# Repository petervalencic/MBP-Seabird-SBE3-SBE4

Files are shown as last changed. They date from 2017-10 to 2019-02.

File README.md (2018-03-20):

# Arduino Seabird SBE3 SBE4 

The project contains C/C++ code for Ardiuno Uno and a shield (Eagle project) for SBE-3 and SBE-4 

# SBE 3
Intended primarily for use on moored and fixed-site temperature measuring systems, the SBE 3S can also be used as a component in custom systems or for high-accuracy industrial and environmental temperature monitoring applications. The low noise characteristics of the SBE 3S allow the use of hybrid frequency measuring techniques to obtain rapid sampling with very high resolution; 40 μ°C resolution can be readily obtained at a 6 Hz sampling rate.

CALIBRATION EQUATION

The calibration yields four coefficients (g, h, i, j) that are used in the following equation (Bennett, 1972):

T [°C] = [1 / (g + hln(fo/f) + iln²(fo/f) + jln³(fo/f) )] - 273.15

where T is temperature [°C], ln is natural log function, and f is SBE 3S output frequency [Hz]. Note that fo, an arbitrary scaling term used for purposes of computational efficiency, was historically chosen as the lowest sensor frequency generated during calibration. For calibration results expressed in terms of ITS-90 temperatures, fo is set to 1000. Calibration fit residuals are typically less than 0.0001 °C.

Example Calibration Data (sensor serial number 2213, 30 May 1996):
g = 4.28793855e-03     h = 6.25807786e-04     i = 2.19368239e-05     j = 1.84262924e-06     f0 = 1000.000

# SBE 4
The SBE 4 conductivity sensor is a modular, self-contained instrument that measures conductivity from 0 to 7 S/m, covering the full range of lake and oceanic applications. The sensor has electrically isolated power circuits and optically coupled outputs to eliminate any possibility of noise and corrosion caused by ground loops. Interfacing is also simplified by the square-wave variable frequency output signal (nominally 2.5 to 7.5 kHz, corresponding to 0 to 7 S/m). The sensor offers improved temperature compensation, smaller fit residuals, and faster turn-on stabilization times.

Because of the SBE 4’s low noise characteristics, hybrid frequency measuring techniques (used in Sea-Bird’s CTD instruments) provide rapid sampling with very high temporal and spatial resolution.

CALIBRATION EQUATION

A least-squares fitting technique (including a zero conductivity point in air) yields calibration coefficients for use in the following equation:

Conductivity [S/m] = ( g + hf 2 + if 3+ jf 4 ) / 10 (1 + dt + ep)

where f is instrument frequency [kHz], t is temperature [°C], p is pressure [decibars], and d is thermal coefficient of expansion (3.25 x 10 -06) and e is bulk compressibility (-9.57 x 10 -08) of the borosilicate cell. The resulting coefficients g, h, i, and j are listed on the calibration certificate. Residuals are typically less than 0.0002 S/m.

Example Calibration Data (sensor serial number 2020, 30 May 1997)

Practical Salinity Scale 1978: C(35,15,0) = 4.2914 [S/m]

g = -1.05697877e+01    h = 1.42707291e+00    i = -4.32023820e-03    j = 4.53455585e-04

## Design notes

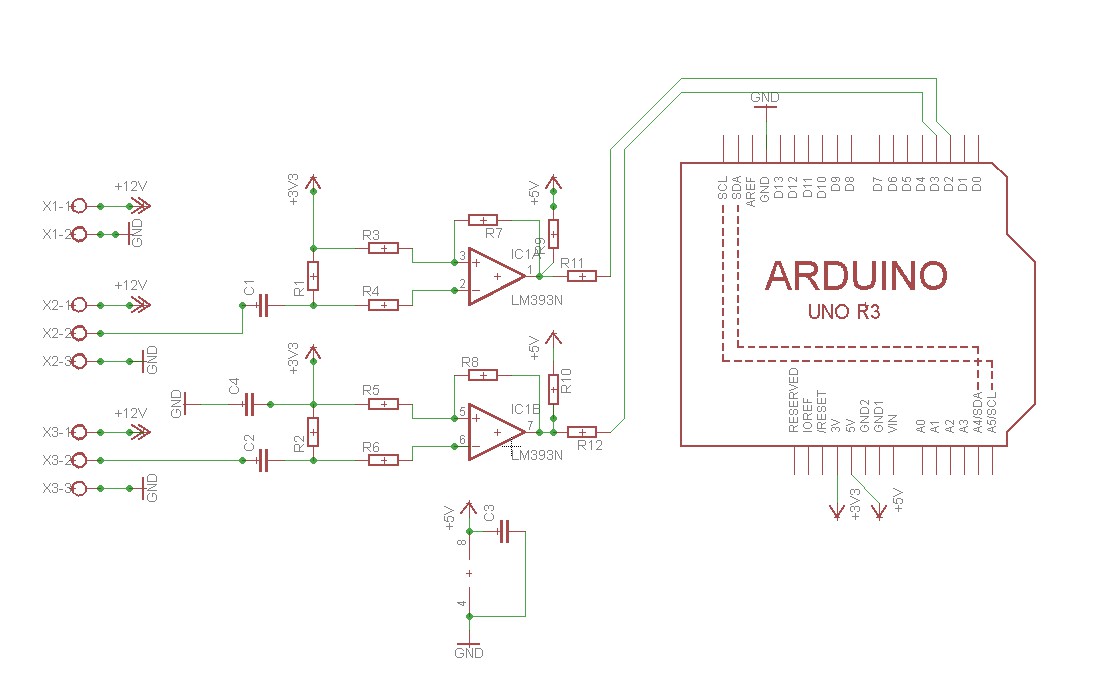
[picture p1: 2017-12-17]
EagleShield/screenshot_1710.jpg

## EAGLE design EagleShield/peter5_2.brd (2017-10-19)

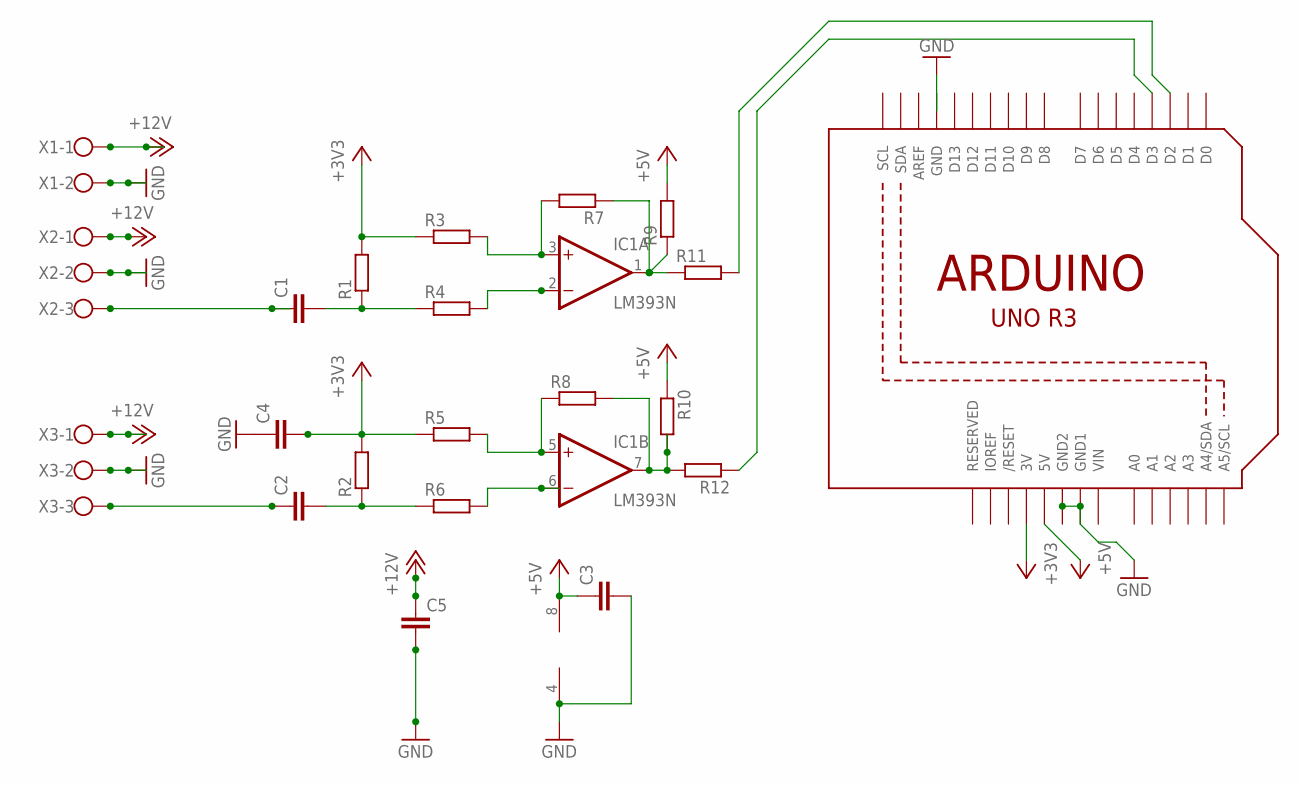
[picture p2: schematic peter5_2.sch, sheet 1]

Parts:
C1, C2, C3, C4: C-EU025-040X050; C025-040X050
C5: C2.5/2; C2.5-2
IC1: LM393N; DIL08; MPN LM393N...
R1, R2, R3, R4, R5, R6, R7, R8, R9, R10, R11, R12: R-EU_0207/7; 0207/7
U1: ARDUINOR3-BPLACE
X1: W237-102
X2, X3: W237-103

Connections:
+3V3: C4.2, R1.2, R2.2, R3.1, R5.1, U1.3V
+5V: C3.1, IC1.8 (V+), R9.2, R10.1, U1.5V
+12V: C5.1, X1.1, X2.1, X3.1
GND: C3.2, C4.1, C5.2, IC1.4 (V-), U1.GND, X1.2, X2.2, X3.2
GND1: U1.GND1
GND2: U1.GND2
unnamed: IC1.3 (+IN), R3.2, R7.2
unnamed: IC1.2 (-IN), R4.2
unnamed: IC1.1 (OUT), R7.1, R9.1, R11.1
unnamed: R11.2, U1.D2
unnamed: R12.1, U1.D3
unnamed: C1.2, R1.1, R4.1
unnamed: IC1.7 (OUT), R8.2, R10.2, R12.2
unnamed: C2.1, X3.3
unnamed: IC1.5 (+IN), R5.2, R8.1
unnamed: IC1.6 (-IN), R6.2
unnamed: C2.2, R2.1, R6.1
unnamed: C1.1, X2.3
VIN: U1.VIN

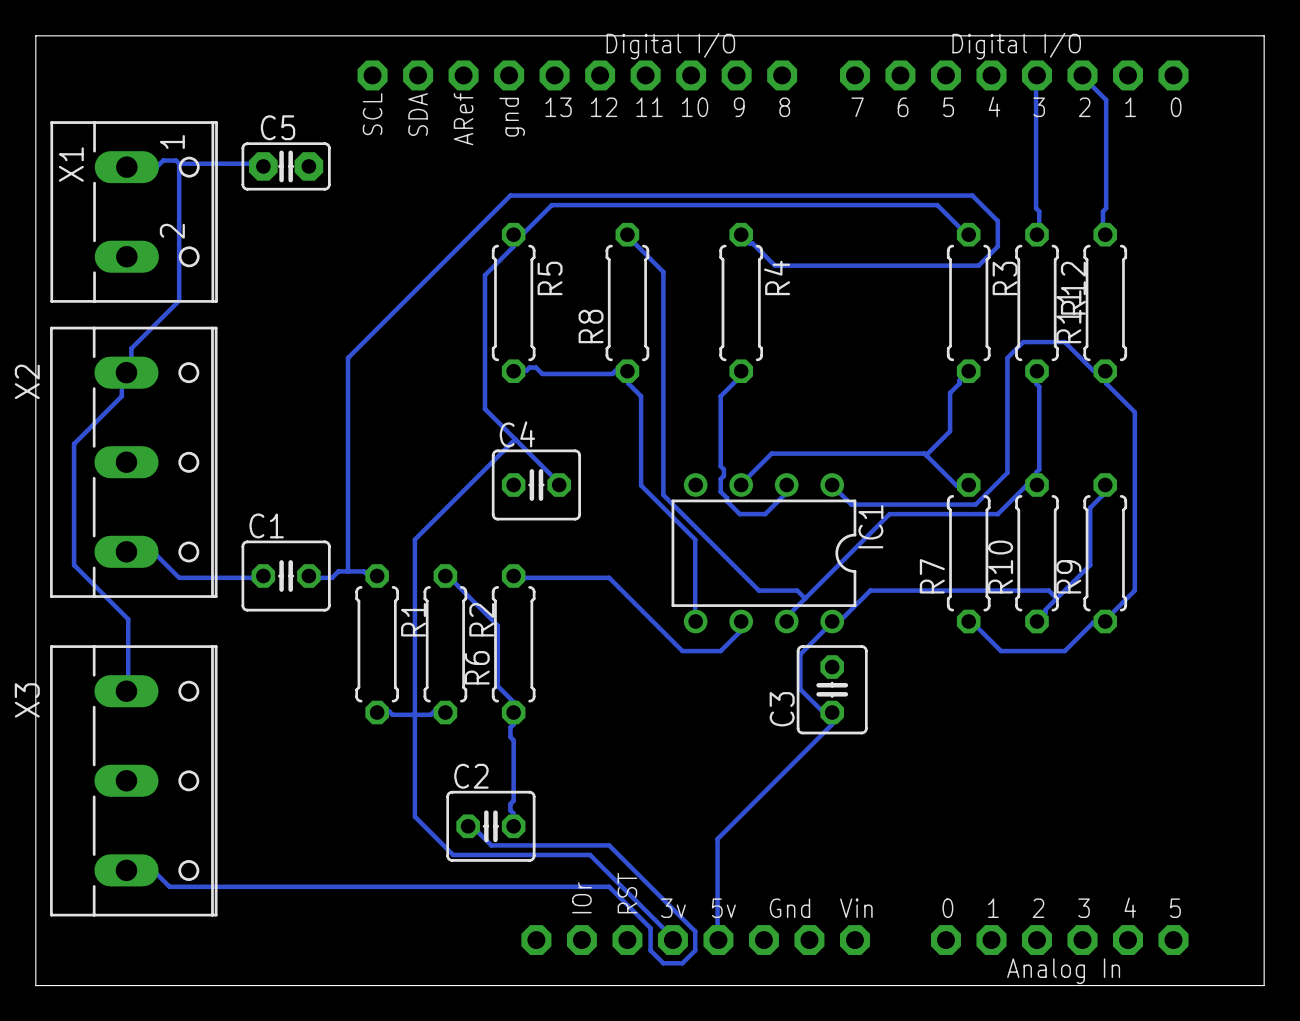
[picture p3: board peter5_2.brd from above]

Board: 2 copper layers, 68.6 x 53.0 mm, 22 parts (0 on the bottom side), 16 nets.

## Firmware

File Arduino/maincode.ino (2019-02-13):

/*****************************************************************
   Merjenje temperature in slanosti s pomočjo
   temperaturne sonde SeaBird SBE-3,
   sonde za slanost Seabird SBE-4 ter miktonotrolerja
   Arduino UNO

   Peter Valenčič, 05.12.2017

   1.) Sprememba preračuna slanosti iz prevodnosti, 15.04.2018
   2.) Dodan Access-Control-Allow-Origin: *, 12.08.2018
 ****************************************************************/

#include < SPI.h > #include < SD.h > #include < Ethernet.h >

//mrežne nastavitve
byte myMac[6];
byte myIP[4];
byte myNM[4];
byte myGW[4];
byte myDNS[4];

//priključne sponke za SBE3 in SBE4
const byte interruptPinTemp = 2;
const byte interruptPinPrevodnost = 3;

//konstante za SBE3
//Kalibrirano Sea-Bird GmbH, SBE3 T121219Mar16
const double g_sbe3 = 4.85442486e-003;
const double h_sbe3 = 6.77400494e-004;
const double i_sbe3 = 2.65502731e-005;
const double j_sbe3 = 2.06782794e-006;
const double f_sbe3 = 1000;

//konstante za SBE4
//Kalibrirano Sea-Bird GmbH, SBE4 C141601Mar16
const double g_sbe4 = -4.10731453e+000;
const double h_sbe4 = 5.02267656e-001;
const double i_sbe4 = -1.63378659e-004;
const double j_sbe4 = 3.70269818e-005;
const double f_sbe4 = 1000;
const double Pcor = -9.5700e-008;
const double Tcor = 3.2500e-006;
const double p = 0;

//pomožne spremenljivke
int timer1_counter;
int cnt_temp = 0;
int cnt_prevodnost = 0;

//frekvenca iz SBE3 in SBE4
int f_temp = 0;
int f_prevodnost = 0;

boolean bPrvaMeritev = false;

boolean bTest = false;

EthernetServer server = EthernetServer(80);

void setup() {
  Serial.begin(9600);
  noInterrupts(); //prekinemo izvajanje interruptov
  //delay(50);
  //določimo vhode za branje frekvence
  pinMode(interruptPinTemp, INPUT_PULLUP);
  pinMode(interruptPinPrevodnost, INPUT_PULLUP);

  //določimo metodo, ki se bo ob prekinitvi izvedla
  attachInterrupt(digitalPinToInterrupt(interruptPinTemp), beriTemperaturo, CHANGE);
  attachInterrupt(digitalPinToInterrupt(interruptPinPrevodnost), beriPrevodnost, CHANGE);

  //nastavimo časovno prekinitev na 1 sekundo pri taktu 16 MHz
  TCCR1A = 0;
  TCCR1B = 0;
  timer1_counter = 34286; // preload timer 65536-16MHz/256/2Hz

  TCNT1 = timer1_counter; // preload timer
  TCCR1B |= (1 << CS12); // 256 prescaler
  TIMSK1 |= (1 << TOIE1); // enable timer overflow interrupt

  // preveri če obstaja SD kartica
  if (!SD.begin(4)) {
    Serial.println("SD card not present...");
    return;
  }

  //prebere datoteko networ.txt, v njej so shranjene mrežne nastavitve
  File fh = SD.open("network.txt", FILE_READ);
  char netBuffer[32];

  int chPos = 0;
  int lineNo = 0;

  //sprehodimo se skozi vse zapise v datoteki in ustrezno zapišemo vrednosti
  while (fh.available()) {
    char ch = fh.read();
    if (ch == '\n') {
      chPos = 0;
      switch (lineNo) {
      case 0:
        if (getMAC(netBuffer, myMac)) Serial.println(F("mac ok"));
        break;

      case 1:
        if (getIP(netBuffer, myIP)) Serial.println(F("ip ok"));
        break;

      case 2:
        if (getIP(netBuffer, myNM)) Serial.println(F("netmask ok"));
        break;

      case 3:
        if (getIP(netBuffer, myGW)) Serial.println(F("gateway ok"));
        break;

      case 4:
        if (getIP(netBuffer, myDNS)) Serial.println(F("dns ok"));
        break;
      }

      lineNo++;
    } else if (ch == '\r') {
      // do nothing
    } else if (chPos < 31) {
      netBuffer[chPos] = ch;
      chPos++;
      netBuffer[chPos] = 0;
    }
  }

  fh.close();

  int x;

  Serial.println("mac ");
  for (x = 0; x < 6; x++) {
    Serial.print(myMac[x], HEX);
    if (x < 5) Serial.print(":");
  }

  Serial.println("ip ");
  for (x = 0; x < 4; x++) {
    Serial.print(myIP[x], DEC);
    if (x < 3) Serial.print(".");
  }

  Serial.println("nmsk ");
  for (x = 0; x < 4; x++) {
    Serial.print(myNM[x], DEC);
    if (x < 3) Serial.print(".");
  }

  Serial.println("gtw ");
  for (x = 0; x < 4; x++) {
    Serial.print(myGW[x], DEC);
    if (x < 3) Serial.print(".");
  }

  Serial.println("dns ");
  for (x = 0; x < 4; x++) {
    Serial.print(myDNS[x], DEC);
    if (x < 3) Serial.print(".");
  }

  Serial.println("Start");
  Ethernet.begin(myMac, myIP, myDNS, myGW, myNM);
  Serial.println(Ethernet.localIP());
  Serial.println("\r\nStart wbs");

  //startamo server socket
  server.begin();

  //omogočimo prekinitve
  interrupts();

}

/**
   Prekinitvena servisna rutina. Izvaja se 1x na sekundo
*/
ISR(TIMER1_OVF_vect) {

  if (bPrvaMeritev == false) return;

  TCNT1 += timer1_counter; //preload časovnika

  //frekvenca iz SBE3 in SBE4
  f_temp = cnt_temp;
  f_prevodnost = cnt_prevodnost;

  bTest = true;
  //resetiramo števce
  cnt_temp = 0;
  cnt_prevodnost = 0;

}

//števec, ki se povečuje v prekinitvi za temperaturo
void beriTemperaturo() {
  cnt_temp++;
}

//števec, ki se povečuje v prekinitvi za slanost
void beriPrevodnost() {
  cnt_prevodnost++;
}

//metoda preračuna temperaturo iz frekvence
double calcTemp(double frekvenca) {
  double f = frekvenca;
  if (f <= 0) return 0;
  double logRes = log(f_sbe3 / f);
  return (1.0 / (g_sbe3 + (h_sbe3 * logRes) + (i_sbe3 * pow(logRes, 2.0)) + (j_sbe3 * pow(logRes, 3.0))) - 273.15);
}

//metoda preračuna prevodnost S/m iz (frekvence in temperature)
double calcPrevodnost(double f, double temperatura) {
  double frek = f;
  double tmp = temperatura;
  if (frek <= 0) return 0;
  frek = frek / 1000; //frekvenco pretvorimo v kHz
  return (g_sbe4 + h_sbe4 * pow(frek, 2) + i_sbe4 * pow(frek, 3) + j_sbe4 * pow(frek, 4)) / 10 * (1 + Tcor * tmp + Pcor * p); //mS/cm = S/m * 10
}

//metoda za preračun slanosti PSU za podano temperaturo, prevodnost in tlak
double calcSlanost(double t, double c, double p) {
  if (c <= 0) return 0;
  double a0 = 0.008;
  double a1 = -0.1692;
  double a2 = 25.3851;
  double a3 = 14.0941;
  double a4 = -7.0261;
  double a5 = 2.7081;
  double b0 = 0.0005;
  double b1 = -0.0056;
  double b2 = -0.0066;
  double b3 = -0.0375;
  double b4 = 0.0636;
  double b5 = -0.0144;
  double k = 0.0162;

  double Aa1 = 2.070e-5;
  double Aa2 = -6.370e-10;
  double Aa3 = 3.989e-15;

  double Bb1 = 0.03426;
  double Bb2 = 0.0004464;
  double Bb3 = 0.4215;
  double Bb4 = -0.003107;

  double c0 = 0.6766097;
  double c1 = 0.0200564;
  double c2 = 0.0001104259;
  double c3 = -0.00000069698;
  double c4 = 0.0000000010031;

  double temp = 1.00024 * t;
  double R = c / 42.914;

  //double rt = c0 + c1 * temp + c2 * temp * temp + c3 * temp * temp * temp + c4 * temp * temp * temp * temp;
  double rt = c0 + c1 * temp + c2 * pow(temp, 2) + c3 * pow(temp, 3) + c4 * pow(temp, 4);

  //double alpha = (Aa1 * p + Aa2 * p * p + Aa3 * p * p * p) / (1 + Bb1 * temp + Bb2 * temp * temp + Bb3 * R + Bb4 * temp * R);
  double alpha = (Aa1 * p + Aa2 * pow(p, 2) + Aa3 * pow(p, 3)) / (1 + Bb1 * temp + Bb2 * pow(temp, 2) + Bb3 * R + Bb4 * temp * R);

  double Rt = R / (rt * (1 + alpha));

  double S = a0 + a1 * pow(Rt, 0.5) + a2 * Rt + a3 * pow(Rt, 1.5) + a4 * Rt * Rt + a5 * pow(Rt, 2.5) + (temp - 15) * (b0 + b1 * pow(Rt, 0.5) + b2 * Rt + b3 * pow(Rt, 1.5) + b4 * Rt * Rt + b5 * pow(Rt, 2.5)) / (1 + k * (temp - 15));

  return S;
}

//Glavna zanka programa
void loop() {

  //prvo meritev izpustimo
  if (bPrvaMeritev == false) {
    bPrvaMeritev = true;
    f_temp = 0;
    f_prevodnost = 0;
    return;
  }

  /*
    if (bTest == true)
    {

      Serial.print("temp:");
      Serial.println(f_temp);
      Serial.print("cond:");
      Serial.println(f_prevodnost);
      bTest = false;
    }
  */
  EthernetClient client = server.available();

  if (client) {
    boolean bTekocaVrstica = true;
    while (client.connected()) {
      if (client.available()) {
        char c = client.read();
        Serial.write(c);
        if (c == '\n' && bTekocaVrstica) {

          //dobimo temperaturo
          double local_temp = calcTemp(f_temp);

          //dobimo prevodnost S/m in preračunamo slanost
          double local_cond = calcPrevodnost(f_prevodnost, local_temp);

          //pri slanosti moramo enoto S/m množiti z 10 da dobimo mS/cm
          //predpostavimo da je tlak 0.2 dBar
          // double local_sal = calcSlanost(local_temp, (local_cond * 10), 0.2);

          client.println("HTTP/1.1 200 OK");
          client.println("Content-Type: text/xml");
          client.println("Access-Control-Allow-Origin: *");
          client.println("Connection: close");
          client.println();
          client.print("<?xml version='1.0' encoding='UTF-8'?><root><temp><value>");
          client.print(local_temp, 3);
          client.print("</value><freq>");
          client.print(f_temp);
          client.print("</freq></temp><sal><value>");
          client.print(calcSlanost(local_temp, (local_cond * 10), 0.2), 4);
          client.print("</value><freq>");
          client.print(f_prevodnost);
          client.print("</freq></sal><cond><value>");
          client.print(local_cond, 4);
          client.print("</value><freq>");
          client.print(f_prevodnost);
          client.print("</freq></cond></root>");
          client.println();
          break;
        }

        if (c == '\n') {
          bTekocaVrstica = true;
        } else if (c != '\r') {
          bTekocaVrstica = false;
        }

      }
    }
    delay(1);
    // zapremo povezavo
    client.stop();
  }

}

//metoda prebere MAC vrednost in jo zapiše v array
byte getMAC(char * macBuf, byte * thisMAC) {
  byte thisLen = strlen(macBuf);
  byte thisOctet = 1;

  thisMAC[0] = strtol( & macBuf[0], NULL, 16);

  for (int x = 0; x < thisLen; x++) {
    if (macBuf[x] == ':') {
      thisMAC[thisOctet] = strtol( & macBuf[x + 1], NULL, 16);
      thisOctet++;
    }
  }

  if (thisOctet == 6) return (1);
  else return (0);

}

//metoda prebere IP naslov in ga zapiše v array
byte getIP(char * ipBuf, byte * thisIP) {
  byte thisLen = strlen(ipBuf);
  byte thisOctet = 1;

  thisIP[0] = atoi( & ipBuf[0]);

  for (int x = 0; x < thisLen; x++) {
    if (ipBuf[x] == '.') {
      thisIP[thisOctet] = atoi( & ipBuf[x + 1]);
      thisOctet++;
    }
  }

  if (thisOctet == 4) return 1;
  else return 0;
}
